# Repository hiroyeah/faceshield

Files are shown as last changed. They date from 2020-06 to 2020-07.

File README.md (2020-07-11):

# はじめに - 3Dプリントフェイスシールド　Wakyu モデル  (学校用)

フェイスシールド 「Wakyu」 モデルは、幼稚園や学校での使用を想定した、3Dプリントでつくるオープンソースのフェイスシールドです。
慶應義塾大学SFC研究所ソーシャルファブリケーションラボ（代表：環境情報学部教授　田中浩也）の、湯浅亮平上席所員と、
ラボの卒業生で、現在はエス.ラボ株式会社に所属する脇本智正氏に共同設計され、両名の頭文字から「Wakyu」モデルと名付けられました。

S/M/Lのサイズを用意してあり、改変・配布・販売も可能です（下記のクリエイティブコモンズライセンスに準じてください）。
シールドの上部に「着せ替えシート」を取り付け、ワンポイントのカスタマイズができる設計となっています。

みなさまの使っている姿を見せていただいたり、感想をお寄せいただけいただけるのであれば、SNSで#wakyumodel とハッシュタグをつけて投稿もしくは、
tanakalab-sfc@googlegroups.com にお願いいたします。カスタマイズのアイディアや、実際に使用している姿を見せていただけると大変嬉しいです。

田中浩也/ 湯浅亮平 / 脇本智正  

# 全国の聾学校への寄贈について

なお、このデータをもとにしたフェイスシールドは、プロクター・アンド・ギャンブル・ジャパン(P&G)株式会社、エス．ラボ株式会社、株式会社丹青社、テラサイクルジャパン合同会社、ナノダックス株式会社と当ラボの連携のもと、約１万個が3Dプリントされ全国の聾学校等へ寄贈されました。1万個の高速量産には、エス．ラボ株式会社の3Dプラント(12連3Dプリンタ量産システム)が活用されました。[その動画はこちらから見ることができます。](https://youtu.be/kBtXUk4LydI)

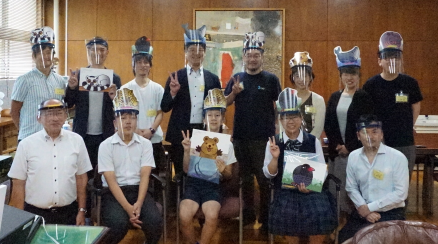
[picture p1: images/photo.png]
2020年6月29日 京都府立聾学校への寄贈の様子


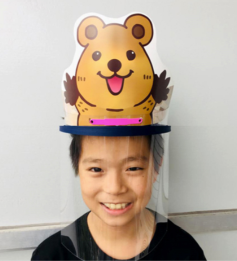
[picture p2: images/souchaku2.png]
実物イメージA
 画像提供：P&G

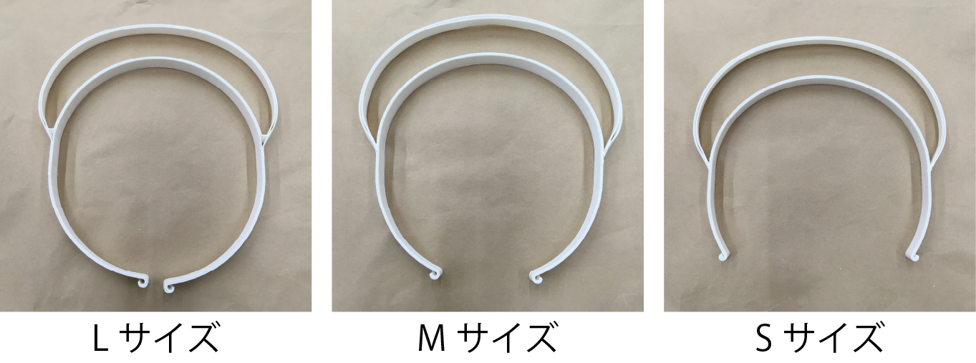
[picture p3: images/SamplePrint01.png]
実物プリント


クリエイティブコモンズCCBY

# プロジェクトパートナー関連リンク

・[プロクター・アンド・ギャンブル・ジャパン株式会社によるプレスリリース　(本取り組みの背景および参画各社の役割) ](https://prtimes.jp/main/html/rd/p/000000031.000031986.html)

・[丹青社による独自サイト (フェイスシールドの着せ替えシートデザインの無償公開) ](https://www.tanseisha.co.jp/news/info/2020/post-33843)

・[エス．ラボ株式会社　(フェイスシールドそのものの注文・購入を希望する場合)](http://slab.jp/)

・[エス．ラボ株式会社 3Dプラント (12連3Dプリンタ量産システム)  ムービー](https://youtu.be/kBtXUk4LydI)

# 公開した3Dデータの説明

フィラメント式のデスクトップ3Dプリンタで出力する場合、フォルダに公開したデータのうち　[Wakyu_Large.stl](Wakyu_Large.stl)が大サイズ、[Wakyu_Middle.stl](Wakyu_Middle.stl)が中サイズ、[Wakyu_Small.stl](Wakyu_Small.stl)が小サイズになっています。どのデータも「透明シールド」を差し込むための溝の設計がカギです。スライス時に、その「溝」をサポート材で埋めたりせずに、かつ寸法通り正しい幅で出力するために、3Dプリンタのノズルは0.4mmを強くお勧めします。

# 使用可能なフィラメント

繰り返し使用するためには高温消毒・アルコール消毒が可能で、かつ頭部に柔らかいPP (ポリプロピレン）が有力であると考えられます。
PP (ポリプロピレン）のフィラメントのうち、安定した3Dプリントを行うために収縮抑制のグラスウールを混ぜたナノダックス社の「3D-MAGIC」をお勧めします。
[ナノダックス社「3D-MAGIC」](http://nanodax.jp/3Dfilament.html)

# シールド部について(材質・型紙)

本Wakyuモデルは 透明度が非常に高く、除菌・消毒作業に対応する為、ポリカーボネートを使用したシールドを用いております。
シールドの大きさは 横 265 mm × 高さ250 mm です。
シールド留め具の寸法は一般的なパンチの穴径・距離になっています。
書類留めに使うバンドなどをお使いください。

ポリカーボネート製シールド部分の単品販売も行う予定ですので、お問い合わせください。
[販売サイト”秘密基地”](https://item.rakuten.co.jp/auc-himitsukichi/c/0000000001/)

多くの方にお使い頂けるよう、シールド部分は大きめに作成しております。
カットをするための型紙を用意いたしましたので、ダウンロードしプリントしてお使いください。
A3用紙で印刷することで、適切な型紙サイズとしてお使い頂けます。
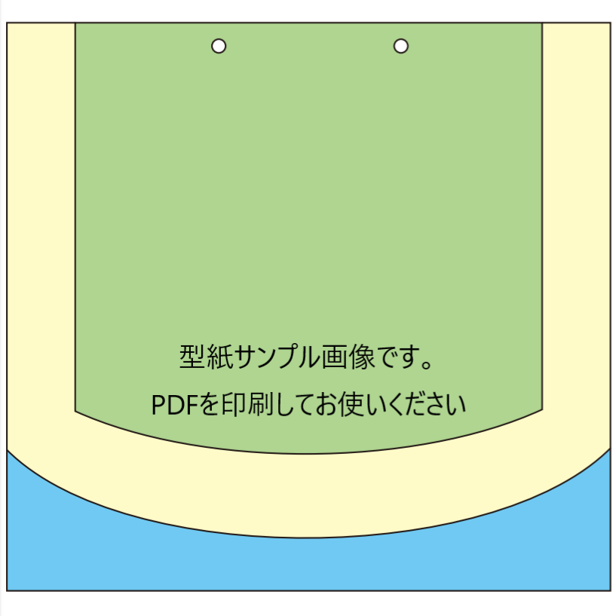
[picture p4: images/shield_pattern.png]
シールド型紙


# 印刷設定(スライサーの設定)

フェイスシールドを一般的なフィラメントタイプのプリンターでプリントするには細かな印刷設定が必要です。
いくつかのパラメータを変更することで、印刷時間を短縮し、より仕上がりが良く着け心地の良いフレームをプリントする事ができます。

２つのスライサーのお勧めする印刷設定を紹介します。

### [Simplify3D](https://www.simplify3d.com/)での詳細設定

#### アウトラインは2層が推奨です
スタート地点を固定することで、短時間かつ、美しい造形が可能です。
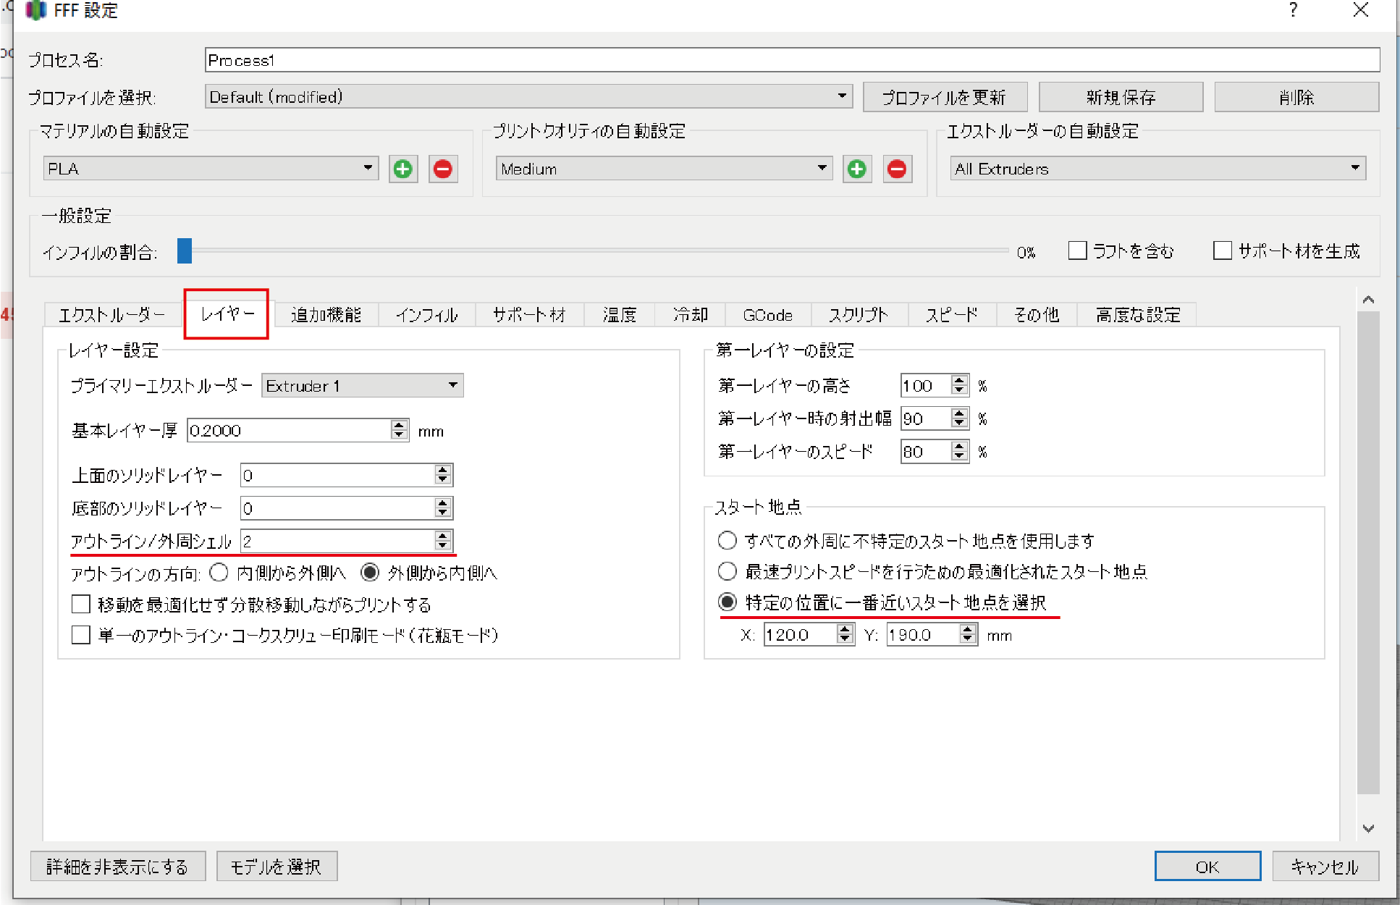
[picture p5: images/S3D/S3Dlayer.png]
S3D_Set1


#### インフィルはできるだけ0%にしてください
印刷後に壁の接着が弱い場合は”アウトラインの重なり”の数字を大きくすることで、接着具合が上がります。(上げすぎ注意)
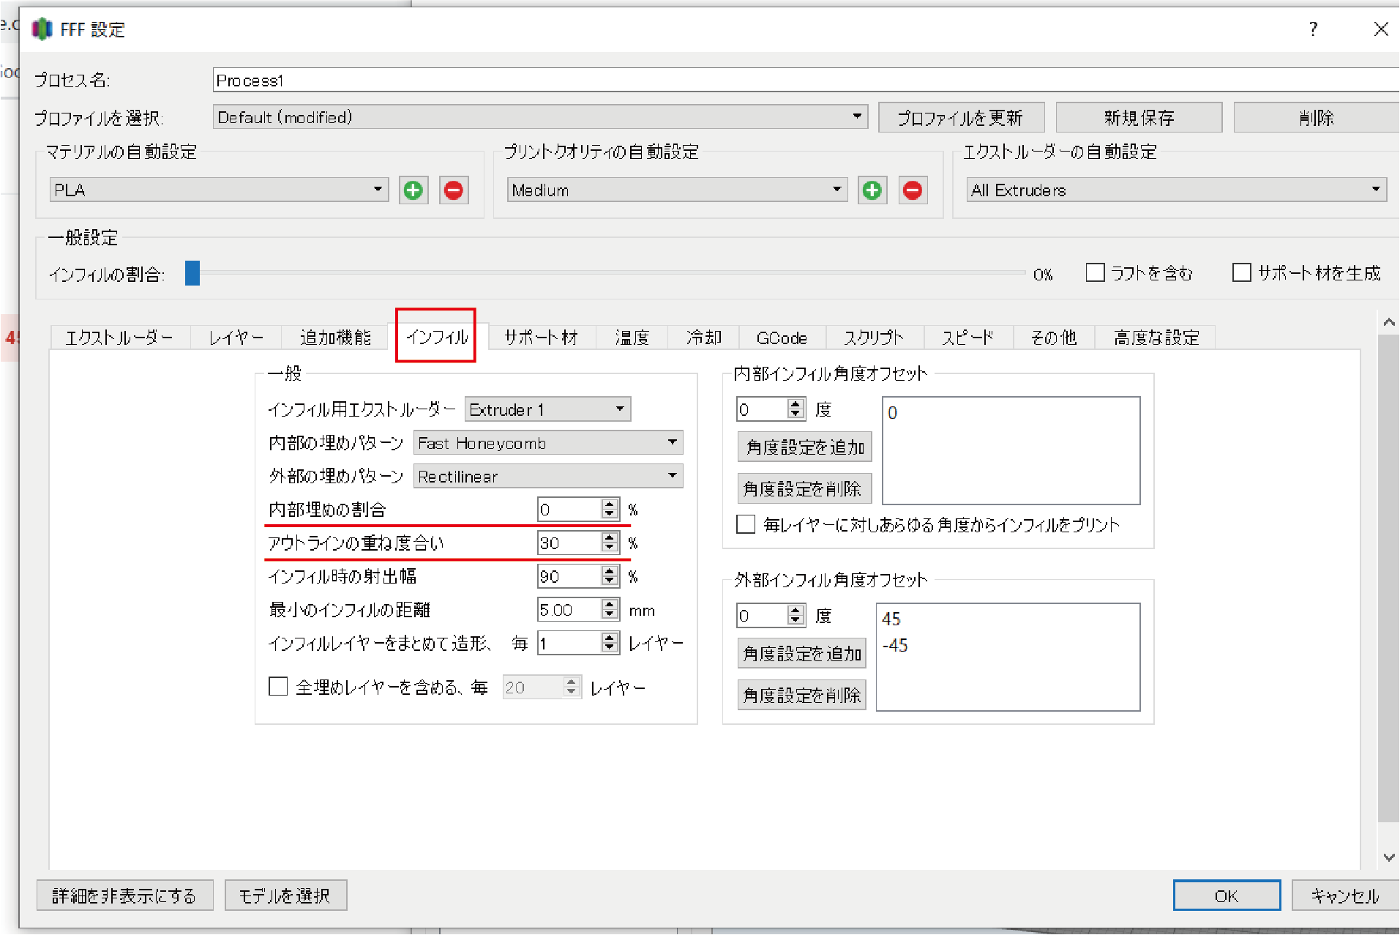
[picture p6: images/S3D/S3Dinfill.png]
S3D_Set2


#### ※モデルが非常に薄い為、高度な設定の”薄壁生成時の動作”を必ず変更し、画像のようにしてください。
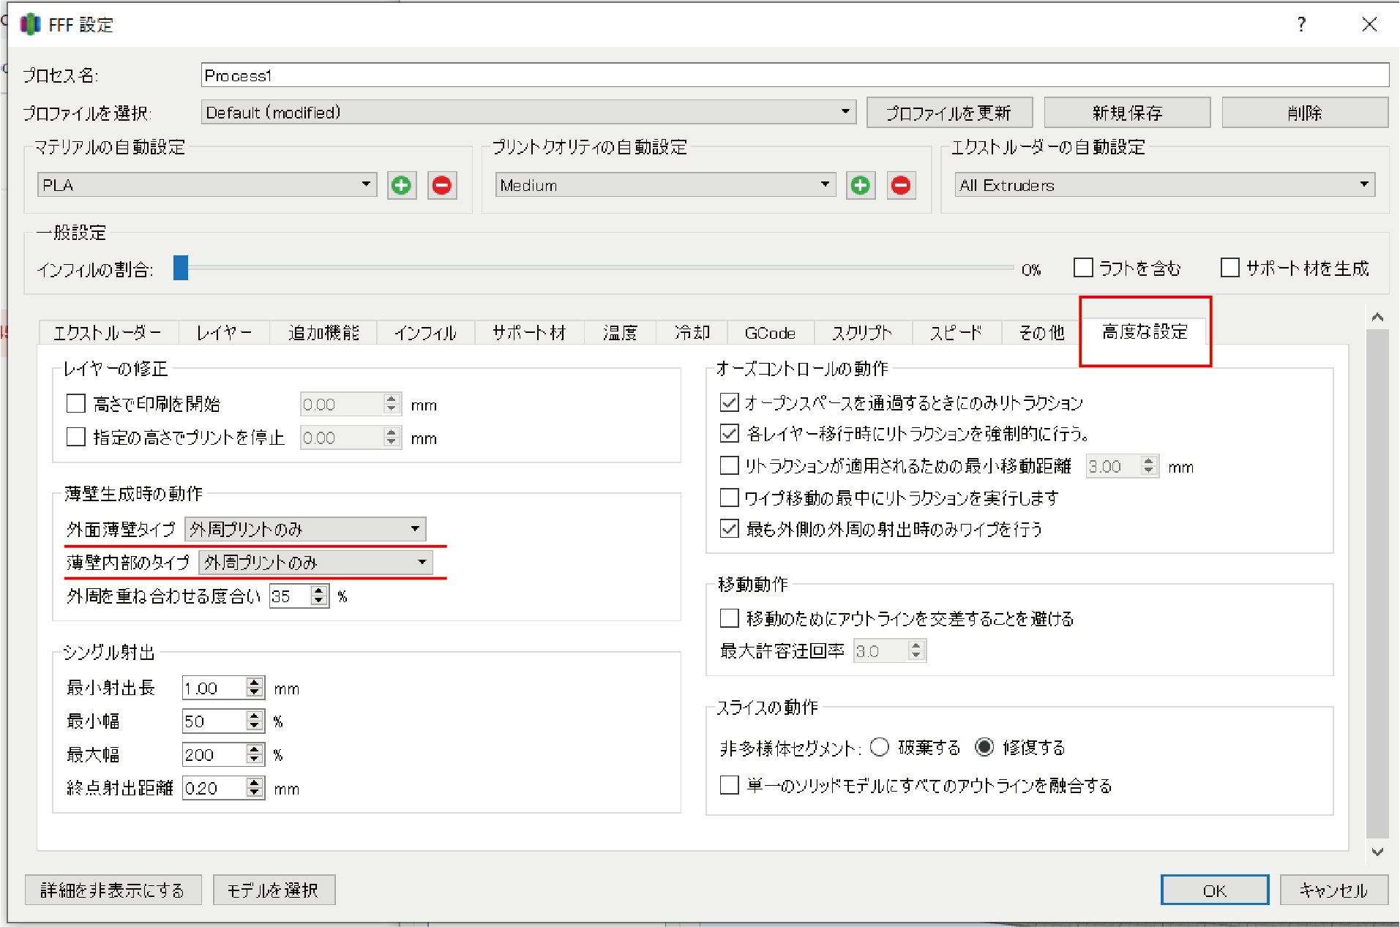
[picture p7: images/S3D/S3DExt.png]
S3D_Set3


#### スライスした状態
フレーム全体
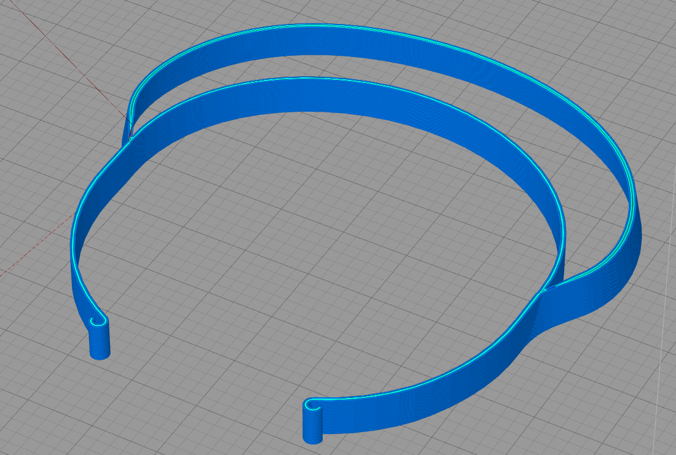
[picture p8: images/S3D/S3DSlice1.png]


スリット部分
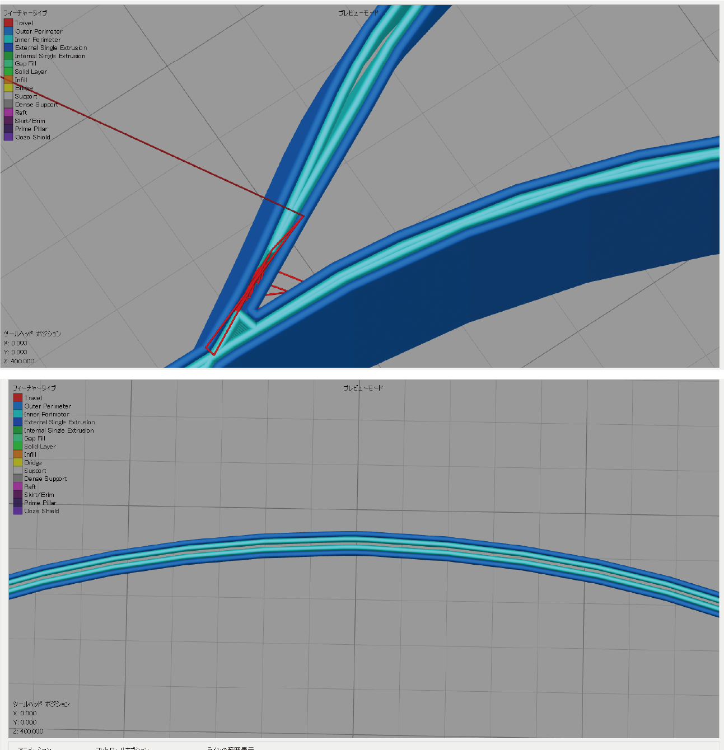
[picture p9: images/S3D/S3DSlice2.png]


### [Ultimaker Cura](https://ultimaker.com/ja/software/ultimaker-cura) での詳細設定

#### Curaの設定を変更する。
(EN) Preferences   -> Configure Cura  -> Setting
(JP) プレファレンス -> Curaを構成する　 -> 設定
からスライス設定の項目を追加する。
Basicの状態からいくつかを追加するだけで良いです。

#### 印刷設定のサンプル
重要な設定ポイントは、Line Width とWall Line Count です

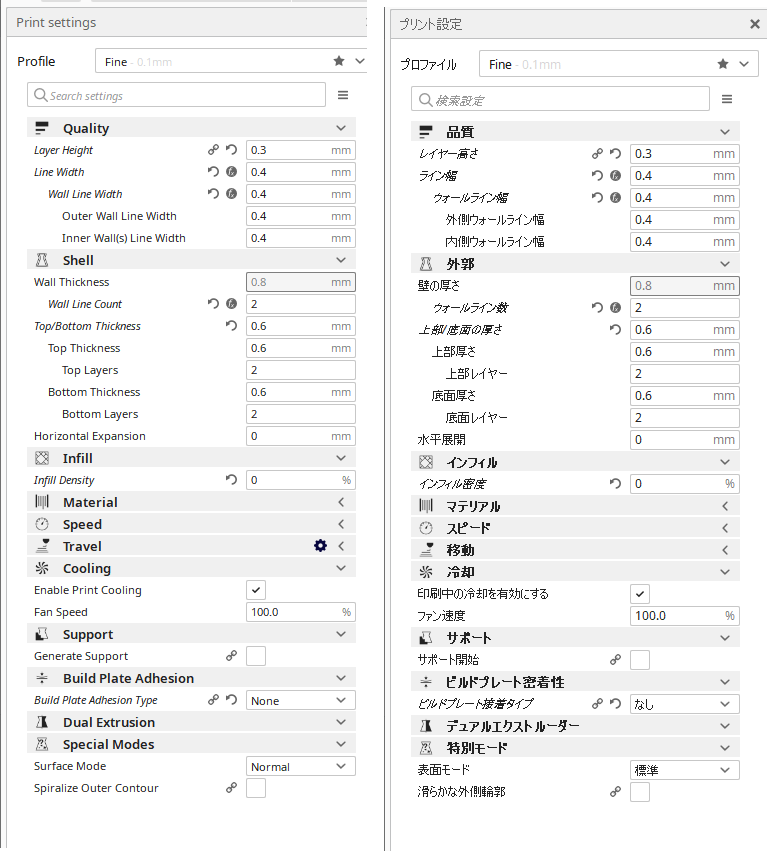
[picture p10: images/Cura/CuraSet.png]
Cura_Set1


スライスサンプル
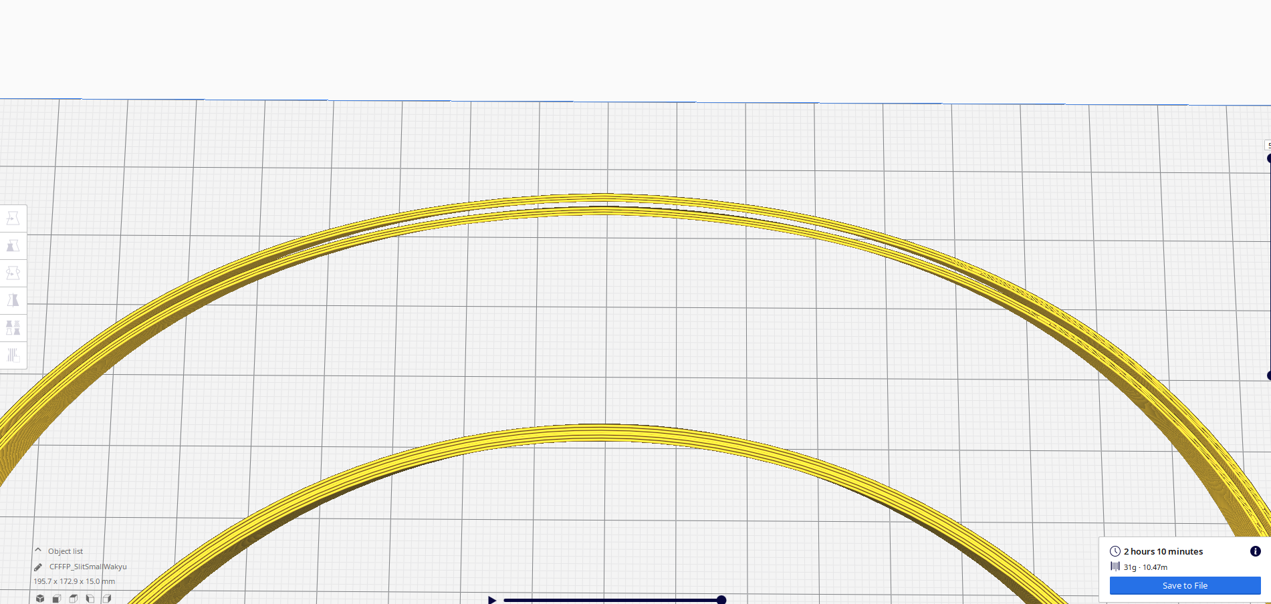
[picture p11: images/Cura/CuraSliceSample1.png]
Cura_Sample1

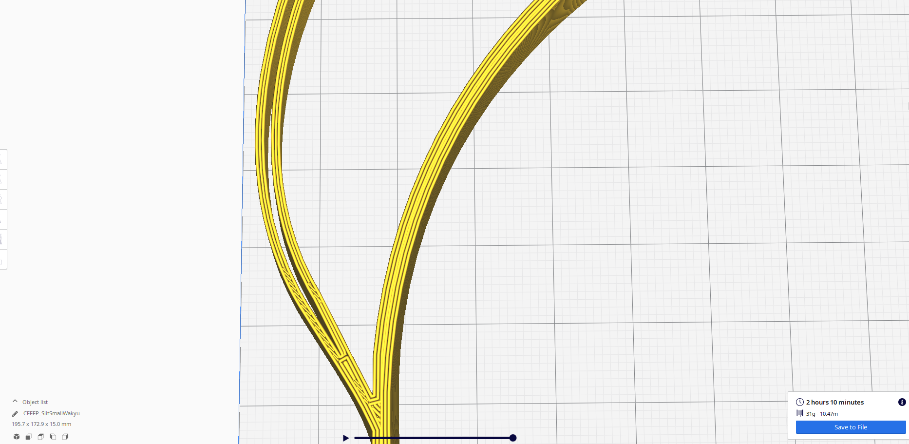
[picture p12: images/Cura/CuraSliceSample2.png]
Cura_Sample2


# 作ったものを他人に渡す場合の注意

[フェイスシールドを安全に作って渡すためのガイドラインドキュメント](https://fabsafehub.org/faceshield)

# （研究開発中）パラメトリック・モデル (Thingiverse Customizr機能への公開)

頭のうらの「つる」の部分の長さだけを自由に改変できる、パラメトリック・モデルを作成し、世界的な3Dデータレポジトリ「Thingiverse」に公開しました（ベータ版です）。https://www.thingiverse.com/thing:4431372

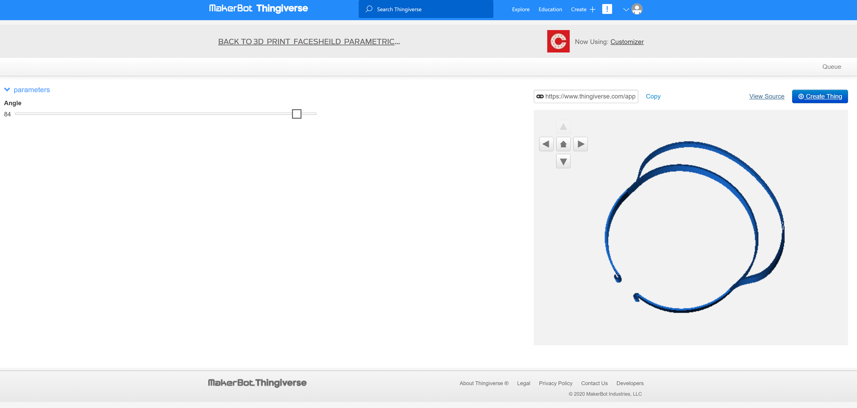
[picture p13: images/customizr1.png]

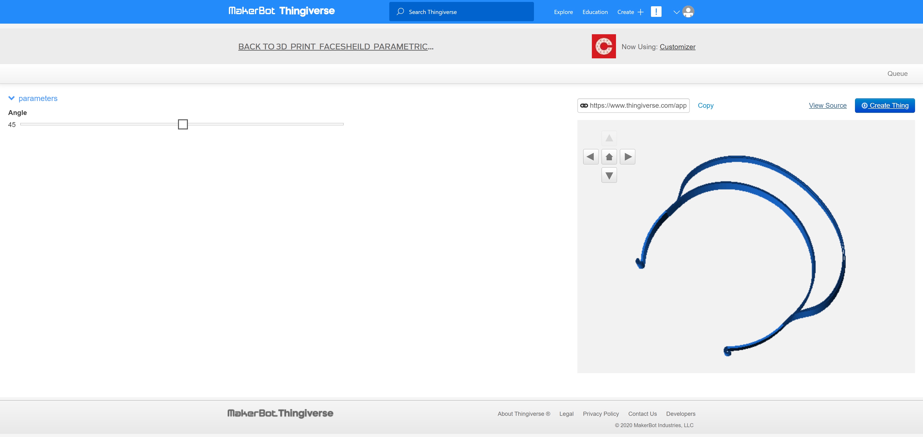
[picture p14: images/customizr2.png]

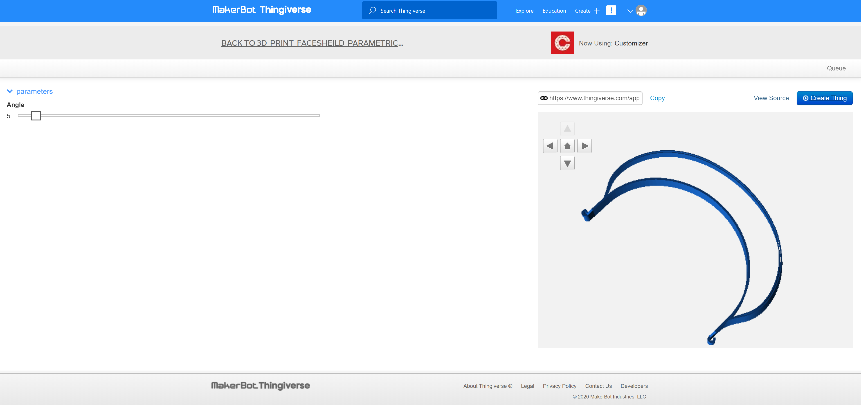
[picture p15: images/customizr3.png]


「Customizer」という機能を使うことで自由につるの長さを変更できます。

# （研究開発中）パラメトリック・モデル (独自のカスタマイズサイトの開発) ※開発中

独自のパラメトリック・モデル改変インターフェイスを研究開発中です。

https://fab.sfc.keio.ac.jp/openjscad/packages/web/

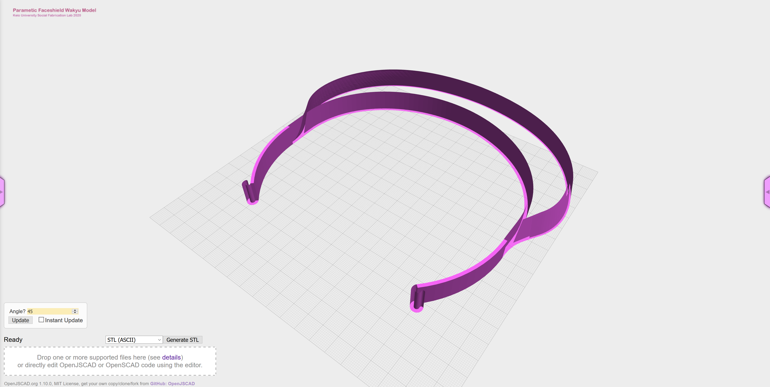
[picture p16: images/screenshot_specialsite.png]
パラメトリック・モデル編集サイト


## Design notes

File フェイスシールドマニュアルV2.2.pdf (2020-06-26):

4

## 使用後の管理

本フェイスシールドを繰り返し使用する際は、感染予防の規定に沿い、必要に応じて感染の専門家等に相談し使 用・管理の検討を行ってください。

① 洗浄・消毒などによる耐久性
「シールドフレーム」は、次亜塩素酸ナトリウム（ハイター・ピューラックス等）での消毒、石鹸を用いた洗浄が可 能です。繰り返しの消毒や使用によって変色・劣化が発生します。3D プリンタ製であるシールドフレームは、浸け ての消毒が推奨されます。熱水での機械洗浄、オートクレーブは使用できません。 「シールド」は、エタノール・次亜塩素酸ナトリウム清拭での消毒が可能です。 「シールド用止め具」は、次亜塩素酸ナトリウムでの消毒（30 分浸漬）、石鹸を用いた洗浄が可能です。 「バンド」は劣化の可能性もありますので毎回取り替えて使用することを推奨します。

② パーツの交換
「バンド」の劣化、紛失などの場合は、雑貨店やインターネットサイト等で販売されている同様の商品を使用するこ とができます。大きめの輪ゴムやゴム紐でも代用可能です。

使用材料について
・フレーム部 | ： (3D プリント製) ポリプロピレン（リサイクルプラスチック）
・シールド | ： ポリカーボネート | ・ゴムバンド | ： ポリウレタン | ・シールド止め具 ： ポリプロピレン

お問い合わせ

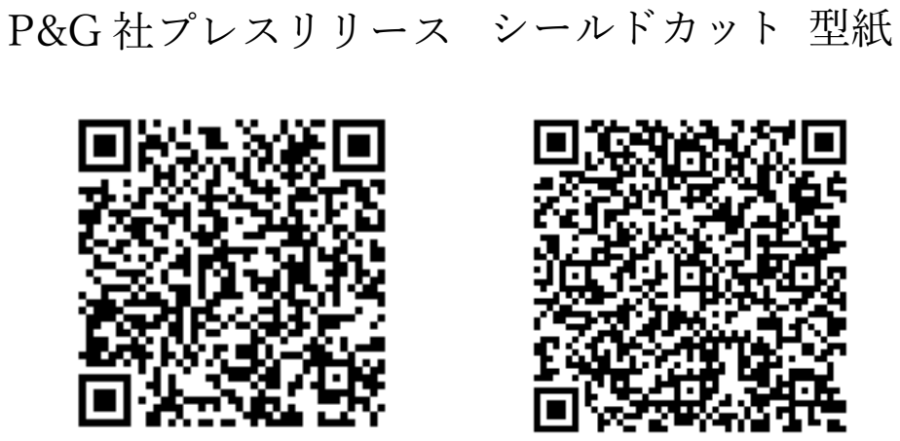
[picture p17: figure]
P&G 社プレスリリース シールドカット 型紙
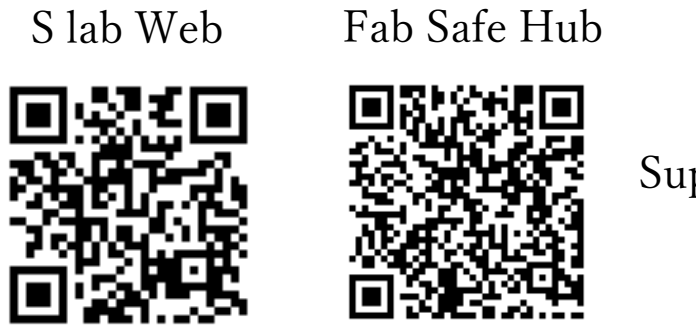
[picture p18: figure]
S lab Web; Fab Safe Hub

使用に際しての不明点などありましたら、下記へ連絡をお願いします。
エス.ラボ 株式会社 http://slab.jp/
〒612-8371 京都府京都市伏見区竹田松林町７４
TEL：075-634-9577 担当 : 脇本(取扱いについて)・橘 (その他のお問い合わせ)

取扱説明書 ver.2.0.0
最終更新日：2020.6.20
Supported by: FabSafeHub

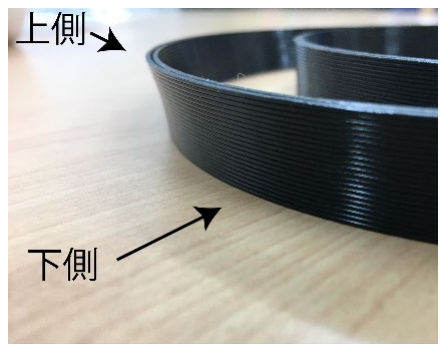
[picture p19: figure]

1

# 3D プリント製 飛沫防止用フェイスシールド “Wakyu“モデル 取り扱い・組み立て説明書

## 使用上の注意

・ フェイスシールドの下部、および開口部から飛沫の侵入は防ぐことはできないため、眼部、鼻腔、口腔粘膜への 付着や顔面への付着による曝露を減少させる事を目的としますが、完全に防ぐことはできません。 ・本取扱説明書に記載されていない使い方をしないで下さい。 ・シールドを付けたままの運動・激しい動きなどによるケガなどに対し一切の責任を負いません。 ・高温環境下での使用、高温になる光源の近くでは使用しないでください。 ・破損した場合は、即時使用を中止して下さい。破損部は鋭利なため、怪我をする可能性があります。

## 本フェイスシールドの構成部品

「1. シールドフレーム」,「2.シールド」,「3.シールド止め具」,「4.バンド」の 4 パーツで構成されています。 シールドフレームは 3D プリンタにて造形、シールドは止め具を付ける為に穴が開いています。
S・M の２サイズがあります | ※ 付属品・色は予告なく変更する場合があります。

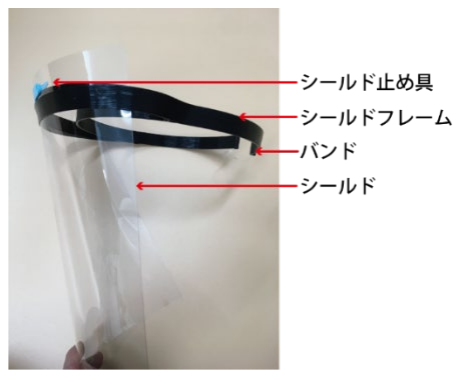
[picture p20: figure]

## 組み立て方

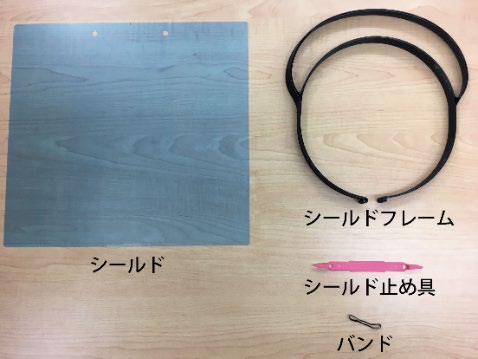
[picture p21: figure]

1. 「シールド」の両面についている青と透明の
保護フィルムを必ずはがして下さい。

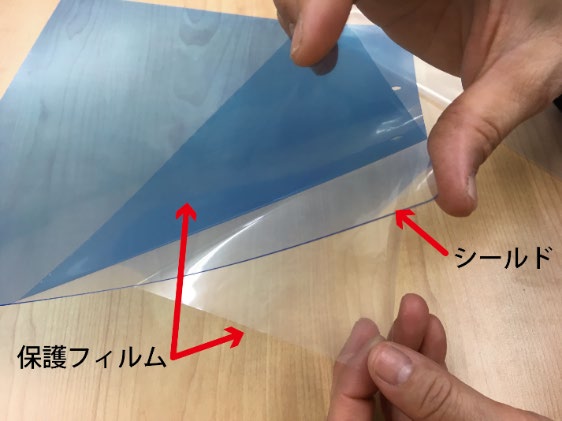
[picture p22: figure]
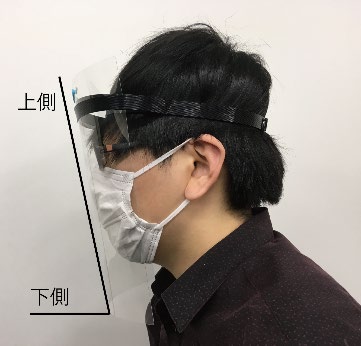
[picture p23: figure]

保護フィルムがはがしにくい場合は、
テープなどを使用して下さい。

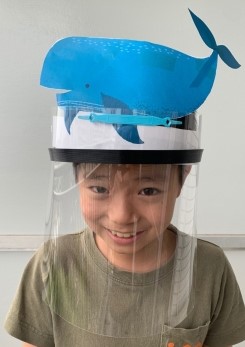
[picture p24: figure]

2. 「シールドフレーム」の向きを確認
３D プリントされたシールドフレームは右下の写真の
ように 角度がついています。そり上がっている方が上
側(頭側)になります。

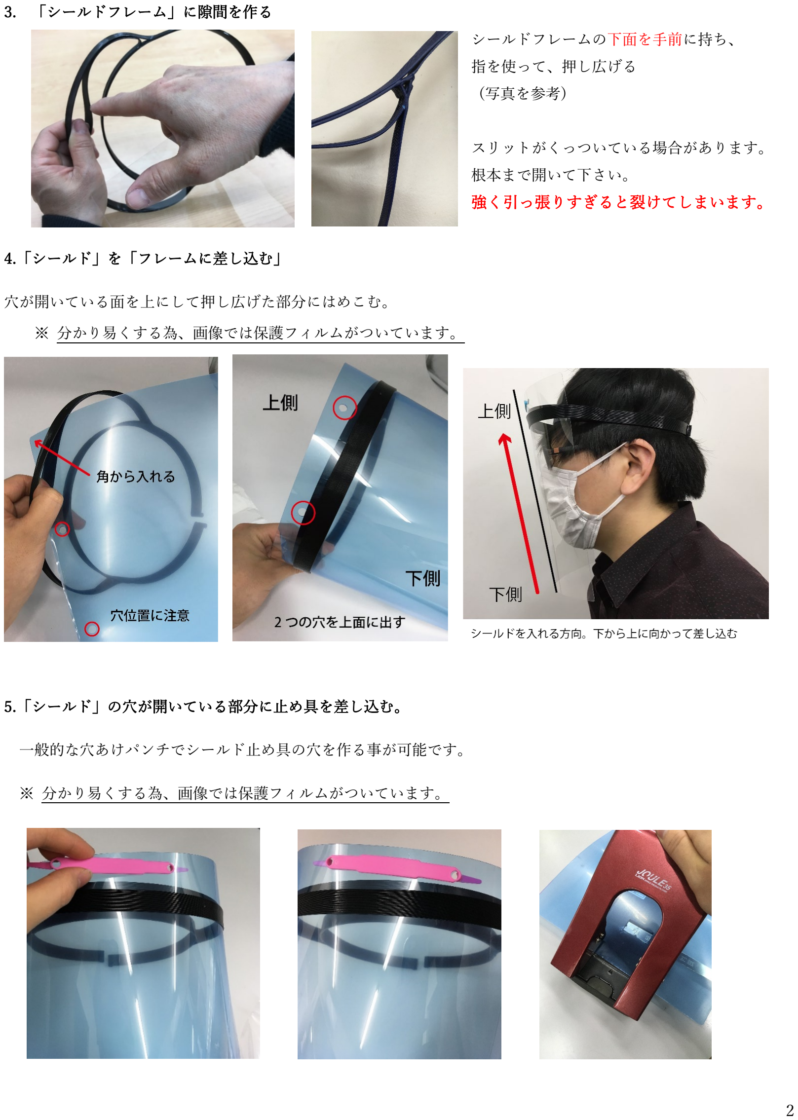
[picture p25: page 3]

2

3. 「シールドフレーム」に隙間を作る
シールドフレームの下面を手前に持ち、
指を使って、押し広げる
(写真を参考)

スリットがくっついている場合があります。
根本まで開いて下さい。
強く引っ張りすぎると裂けてしまいます。

4.「シールド」を「フレームに差し込む」
穴が開いている面を上にして押し広げた部分にはめこむ。
※ 分かり易くする為、画像では保護フィルムがついています。

5.「シールド」の穴が開いている部分に止め具を差し込む。 一般的な穴あけパンチでシールド止め具の穴を作る事が可能です。 ※ 分かり易くする為、画像では保護フィルムがついています。

3

6.ゴムバンドを付ける。
付属している、ゴムバンドを画像のように取り付ける。サイズに合わせて調整下さい。

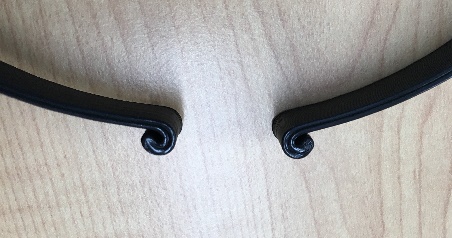
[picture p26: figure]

## 使用前の確認事項

組み立て品の確認

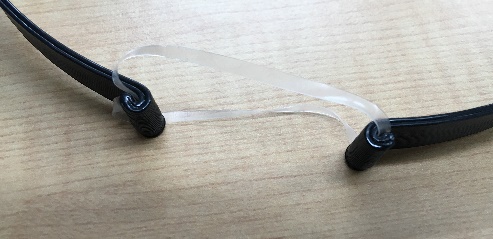
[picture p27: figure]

組み立てたフェイスシールドが正しい状態か確認して下さい。

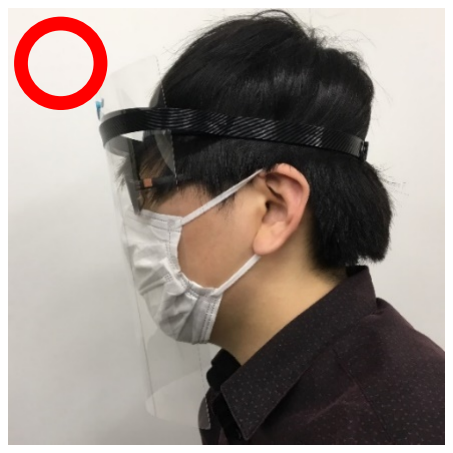
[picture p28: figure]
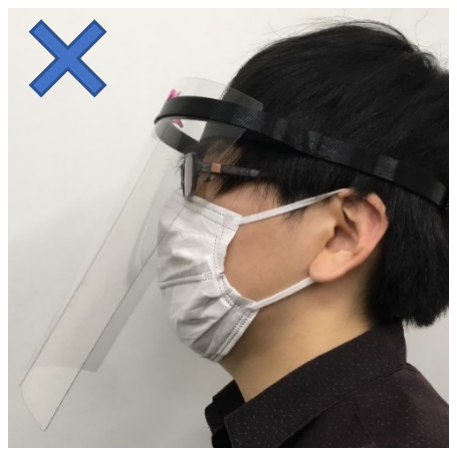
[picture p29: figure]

(フレームの向きが上下逆です) シールドが顔のサイズに適しているか 確認して下さい。

## 使用前の Q＆A

・Q1: シールドがフレームに入らない | A1 : 手で少し開いてください
・Q2 : フレームに青白い部分がある | A2: 力がかかり白くなっているだけです。問題ありません
・Q3 : シールドが大きく使いにくい | A3 : 下記 URL にある型紙を印刷し、カットしてお使いください

## ① 使用前の消毒

梱包・発送時は衛生面に十分配慮しておりますが、使用前に必ず「シールドフレーム」「シールド」「シールド 止め具」すべてのパーツに対し消毒作業をお願いします。

## ② 装着時の使用感の確認

「シールドフレーム」は、細い部分や層部のひび割れ・破損がないか確認をしてください。ハサミなどでカットを して長さを調整する際は、ケガなどに十分注意してください。「バンド」の長さ調整を行い、額から外れず保持でき るか確認してください。装着が不十分な場合は、外れる恐れがあります。

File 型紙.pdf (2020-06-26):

## A3 用紙で 必ず 印刷してください

## ” Wakyu モデル” フェイスシールド シールド形紙

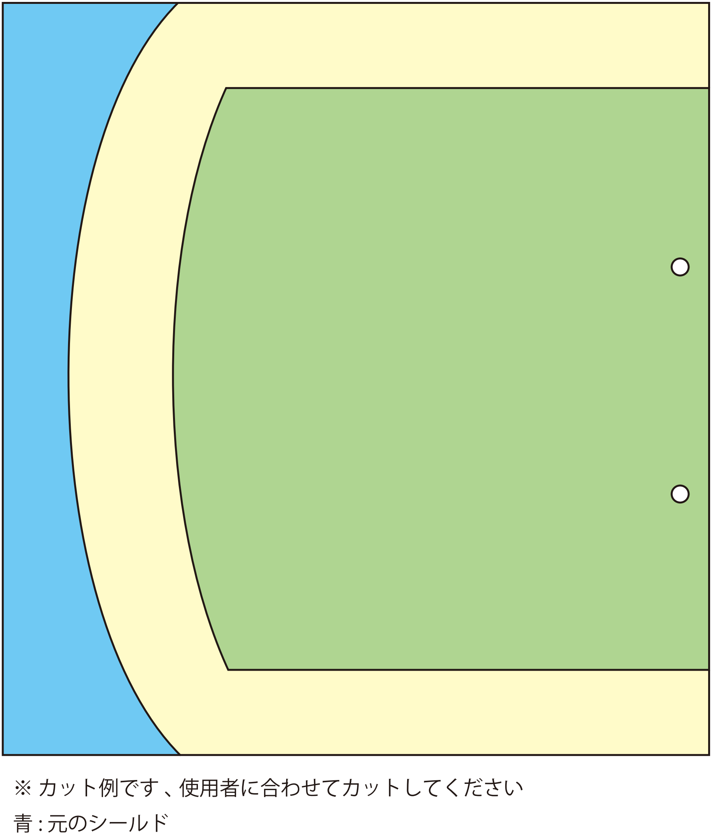
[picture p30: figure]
※ カット例です 、 使用者に合わせてカットしてください 青 : 元のシールド

黄色　:　大人サイズ向け
緑色　:　S サイズ向け
ハサミを使ってカットできます。 切断面は尖りやすく、ケガに注意ください

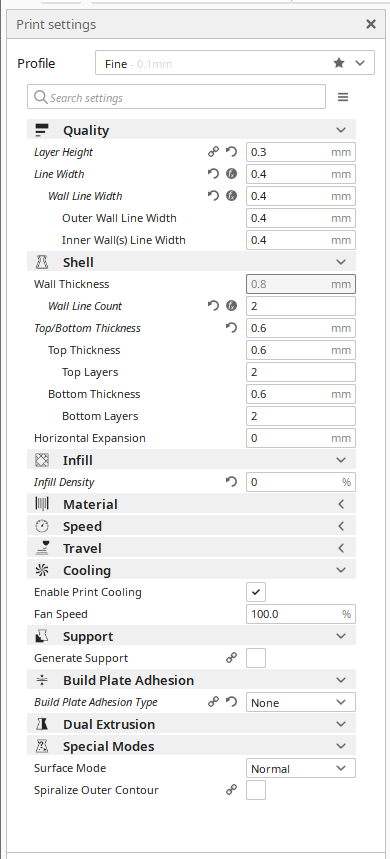
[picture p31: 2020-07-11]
images/Cura/CuraSetEN.png

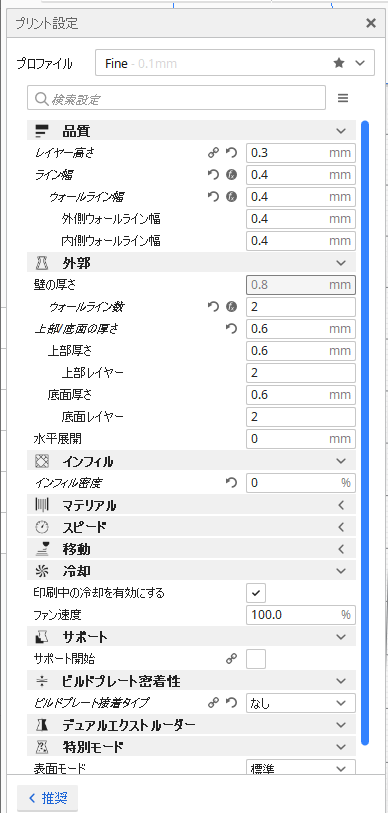
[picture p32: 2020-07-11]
images/Cura/CuraSetJP.png

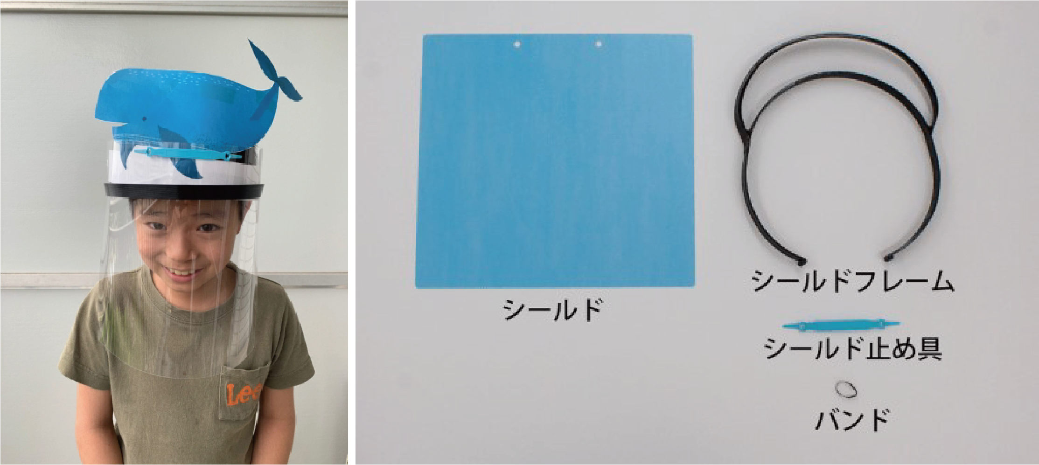
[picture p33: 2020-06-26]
images/FSpartsSample.png

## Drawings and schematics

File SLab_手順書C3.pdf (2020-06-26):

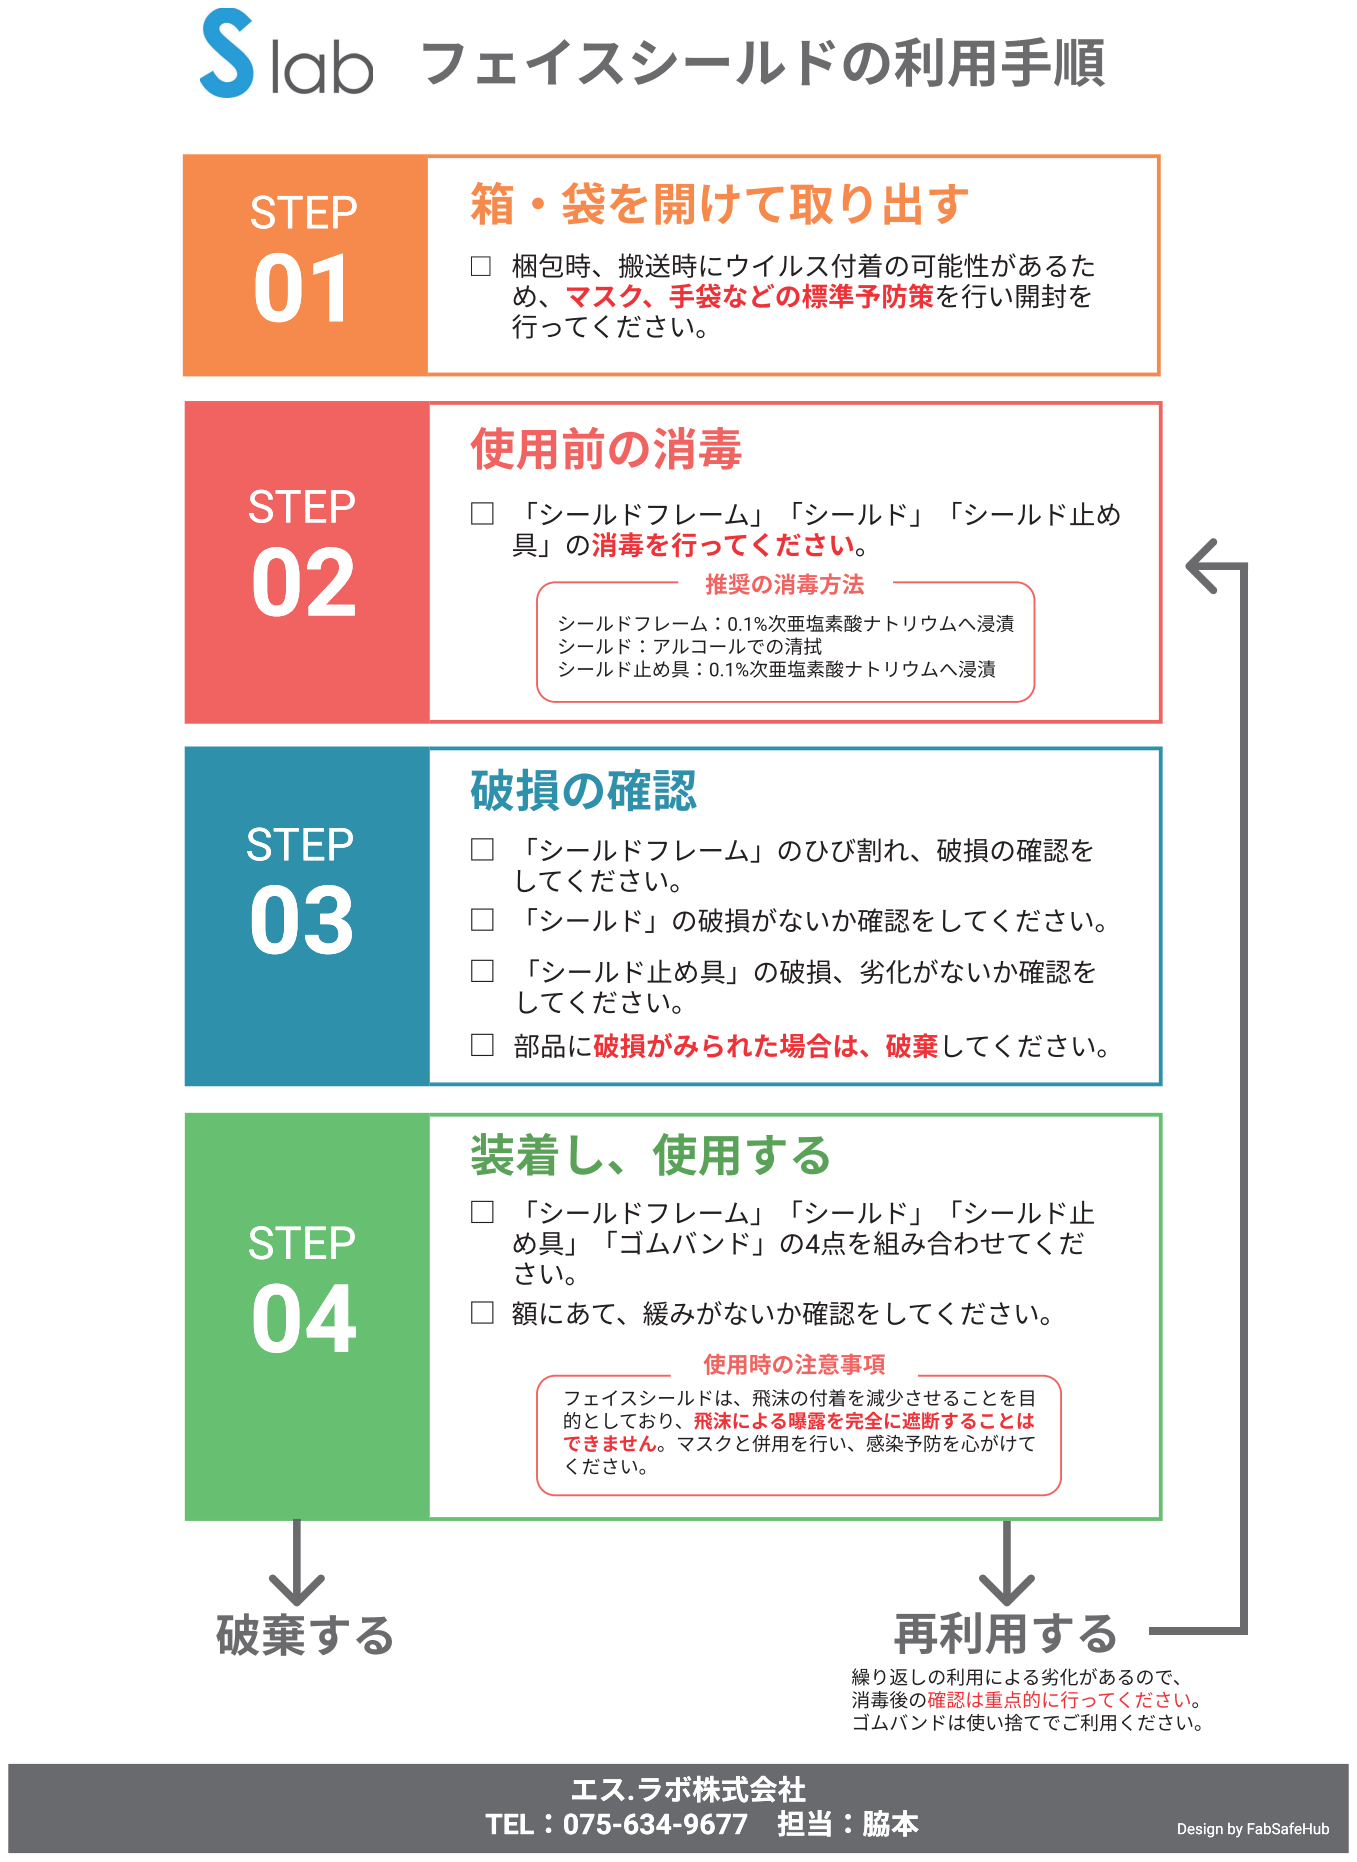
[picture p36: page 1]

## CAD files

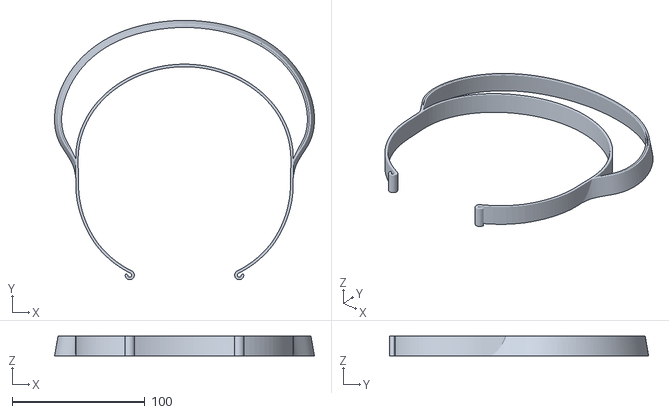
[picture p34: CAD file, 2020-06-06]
Wakyu_Middle.stl
195.5 x 195.1 x 15.0

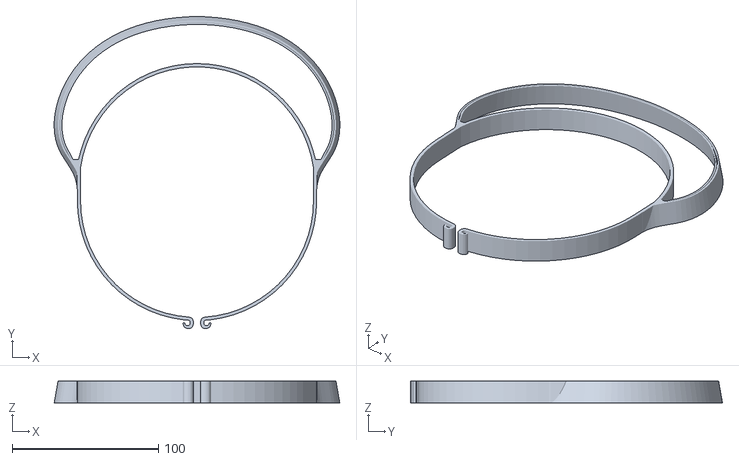
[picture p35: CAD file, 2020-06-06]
Wakyu_Large.stl
195.5 x 213.5 x 15.0
